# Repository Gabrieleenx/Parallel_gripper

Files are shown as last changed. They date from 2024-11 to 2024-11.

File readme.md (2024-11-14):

# Parallel gripper build guide

This is a build guide for the gripper used in the paper "Perception, Control and Hardware for In-Hand Slip-Aware Object Manipulation with Parallel Grippers", preprint available at: https://arxiv.org/abs/2410.19660. Everything is provided as is. 

The main repo for that project can be found at https://github.com/Gabrieleenx/Slip-Aware-Object-Manipulation-with-Parallel-Grippers 

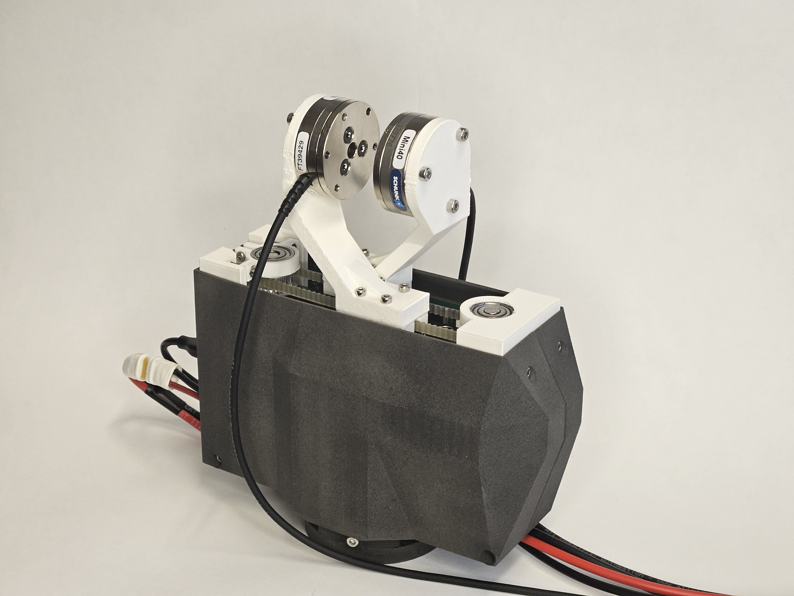
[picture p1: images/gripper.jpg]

## Overview 

This gripper was designed with the goal of having fast low-level force control and a high communication rate with a PC. We are controlling the gripper at 500 Hz, and it is possible to go faster. This readme is organized as follows:

* Overview of construction 
* Overview of code
* Part list
* Build guide

## Overview of construction
The construction of the gripper is fairly simple, it is after all only a parallel gripper. The main selling point is that we are using a bldc motor together with an encoder, which allows us to control it with FOC and get good motor characteristics, we are using SimpleFOC https://simplefoc.com/. The motor is then connected to a 2:1 gear reduction, which dives a pully with a belt on it. The fingers of the gripper run along 2 linear bearings. The motor is controlled by an ESP32 S3 microcontroller. We also deigned a quick connector for the UR10 mount.

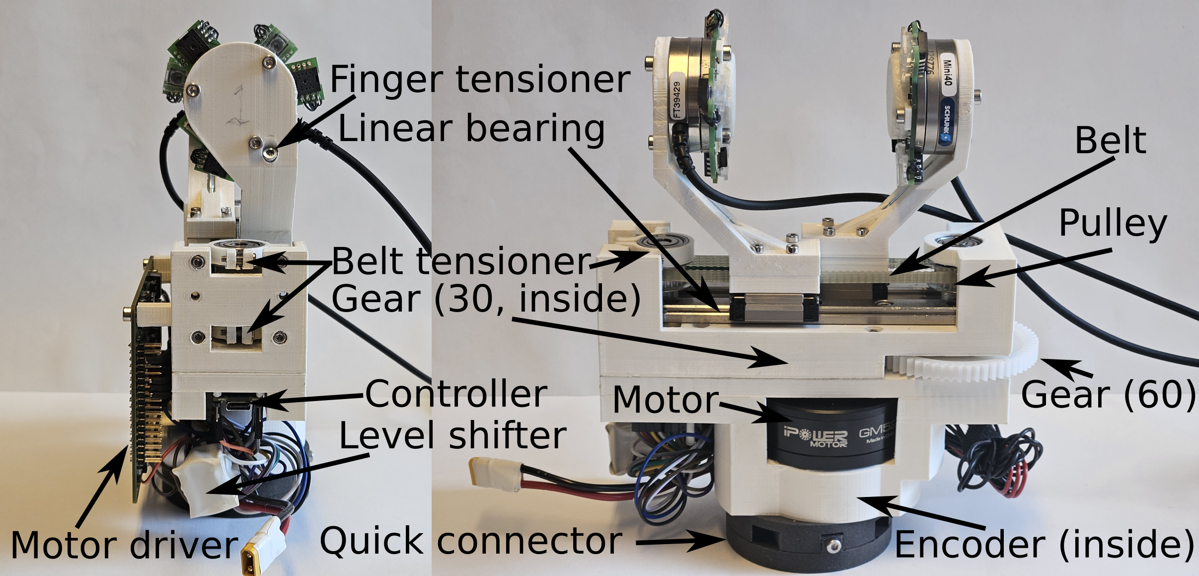
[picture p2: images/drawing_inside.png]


## Overview of code

All the code running on the ESP32 is in the gripper_code folder. The code to communicate with it from a pc can be found at https://github.com/Gabrieleenx/Slip-Aware-Object-Manipulation-with-Parallel-Grippers. The code differs slightly from the simpleFOC library, we implemented our own encoder class, this was to utilize the ESP32 built in pulse counter peripherals, instead of using interupts. And we have a bare minimum serial communication setup. Some of the reasoning to why, is that we had problems with the ESP32 S3 Nano from Arduino, where it would randomly stop commnicating. Unlike many other development boards it does not have a UART to USB chip and the USB communication is handeled internally on the ESP32. To get it to work properly we had to compile our code in debug mode to force it to use another part of the USB peripheral, (there probably is a better solution, but it worked and I had already spent way too much time debugging this).

We are using ardunio IDE 2.3.2 on Ubuntu 20, with simpleFOC library 2.3.4. Compiled with debug mode (Hardware CDC). 

The gripper outputs angle of the motor [RAD], and take commands on target voltage [-20.0 to 20.0], the sign determines the driection. 

## Part list 

### Compnents 

2x NSK Linear Guides LH100120ANK1B01PN1, LH, https://se.rs-online.com/web/p/linear-guides/4979411

1x Arduino nano esp32 (not with pre soldered pins) https://store.arduino.cc/en-se/products/nano-esp32?srsltid=AfmBOoq2j8PJsWTmrSQZ9lXL6lKOGxVrW5B-yabFGoDSFEEn9P-Iw4cd

1x iPower Motor GM5208-24 Brushless Gimbal Motor https://eu.robotshop.com/products/ipower-motor-gm5208-24-brushless-gimbal-motor

1x AMT103-D2048-I8000-S https://www.mouser.se/ProductDetail/Same-Sky/AMT103-D2048-I8000-S?qs=Jm2GQyTW%2FbhTj4QqD8fAHQ%3D%3D&mgh=1&gad_source=1&gclid=Cj0KCQiAoeGuBhCBARIsAGfKY7zdJklvF7jDlw4l8NdwcRQ16M22bnk4nwzr7osbEtRulv0hirsh0TkaAoGrEALw_wcB

1x DRV8302 Motor Drive Module https://www.aliexpress.com/i/4000126430773.html?gatewayAdapt=glo2fra (This is completly overkill and something like https://simplefoc.com/simplefoc_mini_product_v1 would be more appropiate, but was out of stock at the time, if you want current sensing, make sure the driver hardware supports it)

1x OPTIBELT 4 T2,5 / 265 Timing Belt, 106 Teeth, 265mm Length, 4mm Width https://se.rs-online.com/web/p/timing-belts/2171565 

2x OPTIBELT Timing Belt Pulley, Aluminium 4 mm, 6 mm Belt Width x 2.5mm Pitch, 22 Tooth https://se.rs-online.com/web/p/belt-pulleys/2362794 (these do not come pre-drilled!)

1x RS PRO POM 30 Teeth Spur Gear, 1 Module, 6mm Bore Diam, 30mm Pitch Diam, 14mm Hub Diam https://se.rs-online.com/web/p/spur-gears/5217540?searchId=529fef86-fb48-4f9c-933e-d6b7e4e49f6e&gb=s

1x RS PRO POM 60 Teeth Spur Gear, 1 Module, 8mm Bore Diam, 60mm Pitch Diam, 18mm Hub Diam https://se.rs-online.com/web/p/spur-gears/5217641?searchId=f93c0d57-8f67-4b74-b46d-4ea63853b34f&gb=s

1x Bosch Rexroth 0.4m Long Steel Closed Bush Shaft, 6mm Shaft Diam. , Hardness 60HRC, h6 Tolerance https://se.rs-online.com/web/p/linear-shafts/7243399 (This needs to be cut, and it is quite hard, alternativly is to buy an aluminium shaft which is much easier to work with)

I2C level shifter (atleast 2 channels) https://www.electrokit.com/nivaomvandlare-4-kanaler-bidirektionell-i2c?gad_source=1&gclid=Cj0KCQiA_qG5BhDTARIsAA0UHSI5S-Kx_KQxKBlJcykZjvEIinTe4hLcBaB7p3R2S9C23zfkMdlB-KEaAmAnEALw_wcB

### Wires and screws 
M1.6 [2x 6mm]

M2.5 [2x 6mm, 2x 8mm, 2x 10 mm, 8x 16 mm, 4x 20mm]

M3 [13x 8mm, 8x 10mm, 2x 14mm,4x 20mm, 3x 30mm, 1x 40mm, 2x 50mm]

M4 [3x 25 mm (or 20 mm should also work)]

You will need nuts (also 2x square nuts for m3, one for each finger), wires and dupont cables. 

### 3D printed parts
See stl_files folder for all the stl files. Almost all parts are printed in PLA and most with around 30% infil. Some of the parts has been slightly modified from the gripper in the pictures, this minimize the amount of post modification needed to the parts. 

Parts printed in PLA:
* belt_tensioner.stl
* bottom_part.stl
* drill_pully_holder.stl
* finger.stl (printed at 100 % infil)
* finger_base.stl (printed at 100 % infil)
* gear_spacer.stl  (printed at 100 % infil)
* middle_part.stl
* motor_to_gear.stl
* top_part.stl

The following parts where printed with an SLS printer (plastic), but they could be printed with normal FDM printing. 
* body_shell_1.stl
* body_shell_2.stl
* quick_adapter.stl
* UR_10_mount.stl 

The contact pads are printed with dual material
* contact_pad.stl outer part TPU95
* contact_pad.stl inner part PLA

### Other parts

* You will need a powersuply that can deliver 20 V and atleast 1A (preferably more, I use a bench power suply with adjustable volatage and current limits). 
* You will also need to get or create cables to connect the power supply with the motor driver, I have a small connector close to the gripper so that it is easy to diconnect. 
* I would recommed getting velcro strips for cable managment, I bolted some of them under the gipper to reduce forces on the contacts.
* You will need a USB cable, make sure it is a decent cable, otherwise power and communication issues might occure. 

## Build/Assembly guide

This an assembly guide for the gripper, an overview of the parts can be seen below:

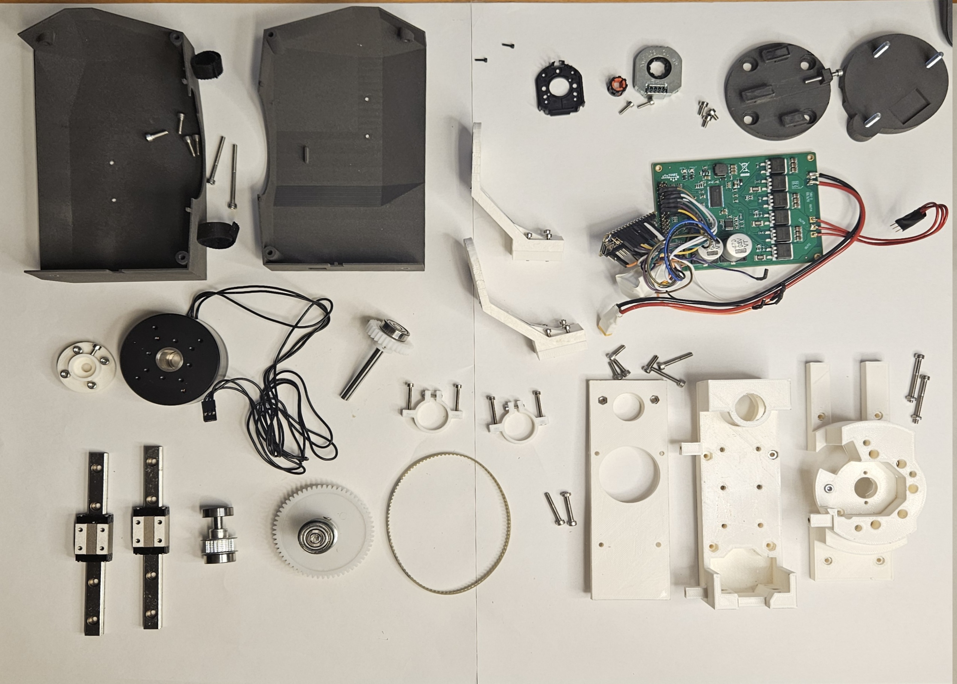
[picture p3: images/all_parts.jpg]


Start with cuting the 6mm shaft into 34mm, 60mm, and 48 mm lengths.  
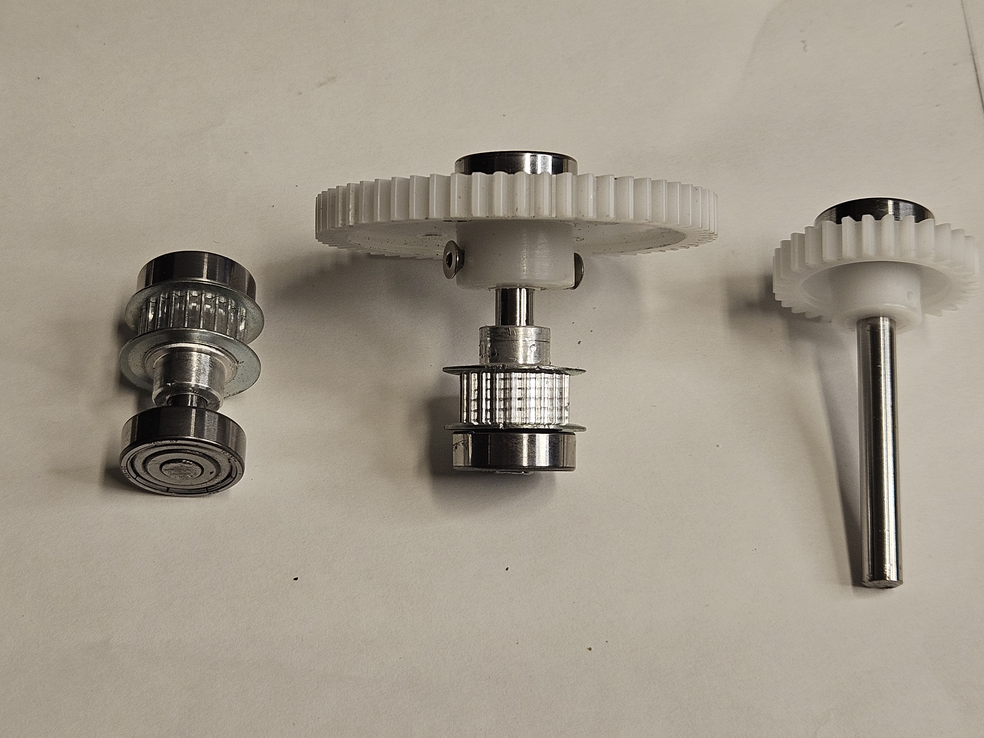
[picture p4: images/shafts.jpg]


Then drill 6mm holes in the pulley, they will be pressfitted on, so sligthly smaller than 6mm is preferable. You can use the 3D printed fixture to secure the pulley when drilling. It is important that the hole is in the center and straight, would recomend using a pillar drill.  

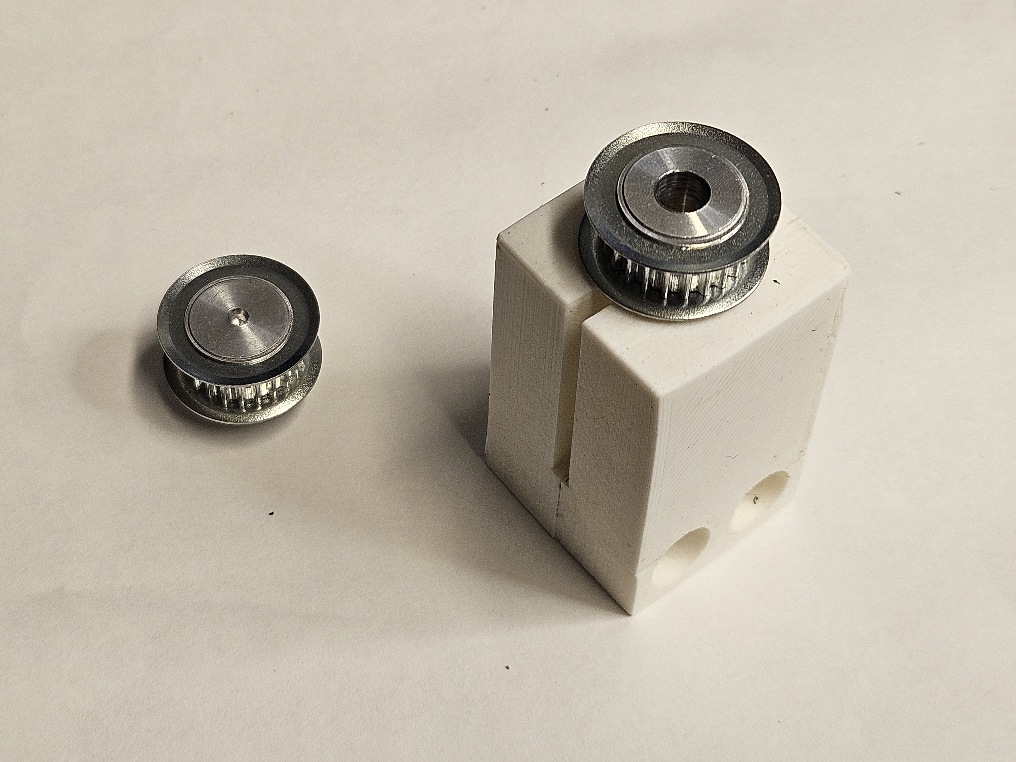
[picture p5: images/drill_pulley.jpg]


Put pulleys and bearings on, the gear big gear is put on with a spacer (3D printed) and two 2.5 mm diameter holes are drilled into the base of the gear, in each hole a M3, 6mm thread lenght countersunk screw are screwed in. The shaft is filed with flat spots for the scres to press against. The pulley is put on by pressfit and is tapped with a hammer at the base to secure it. 

2x m3 6mm thread countersunk screws. 

Insert M3 nuts,

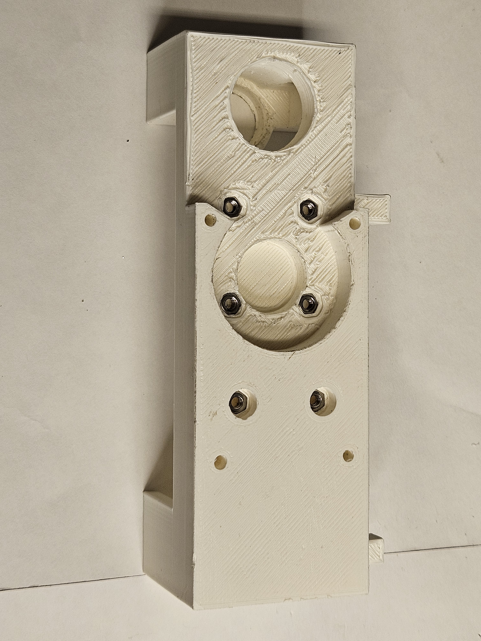
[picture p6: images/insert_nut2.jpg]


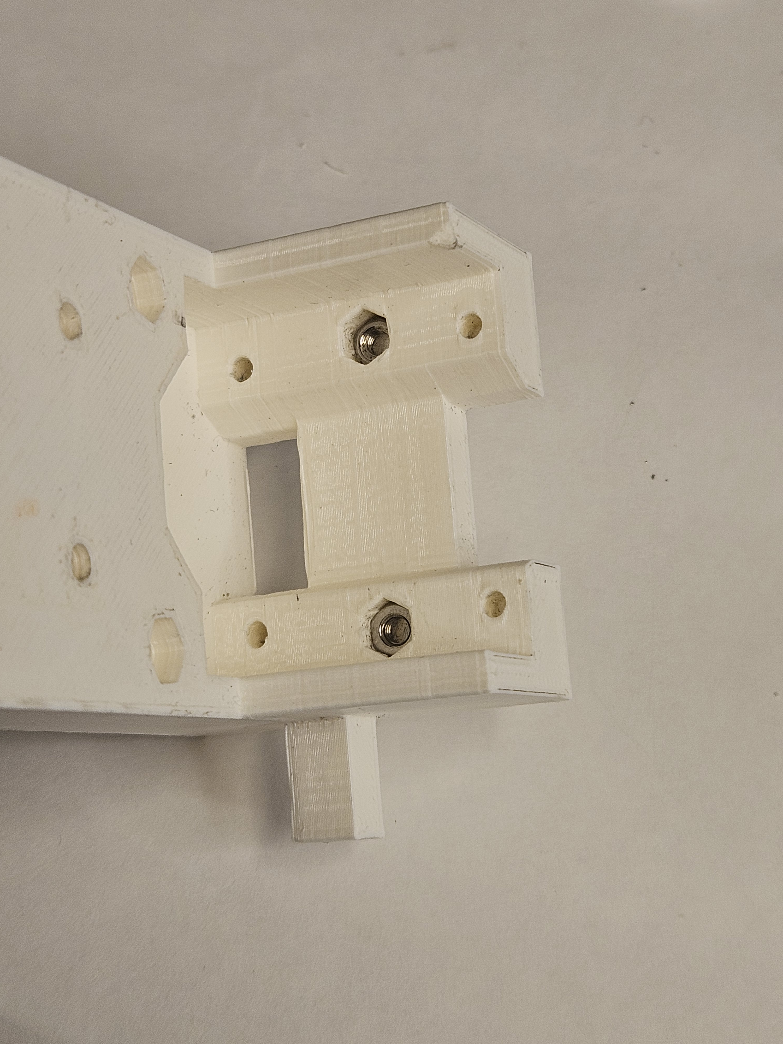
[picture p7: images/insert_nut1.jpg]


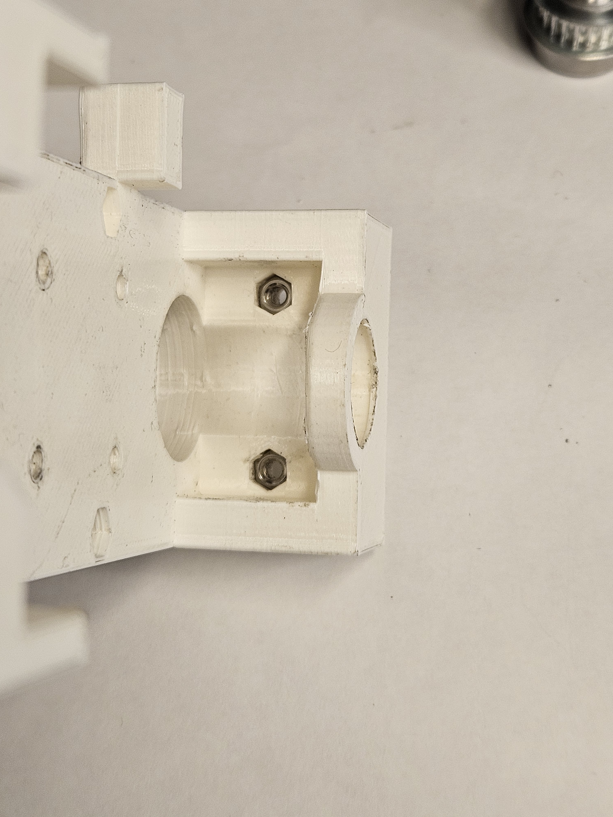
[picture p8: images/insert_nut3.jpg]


Insert the shaft with the big gear to the top part, and with the belt on.

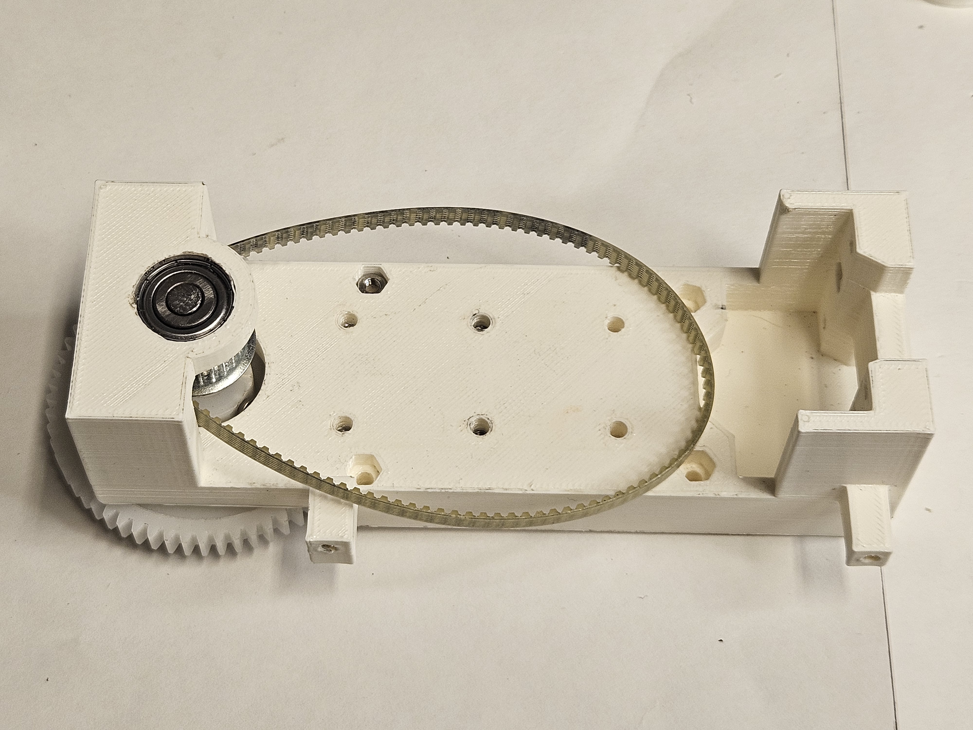
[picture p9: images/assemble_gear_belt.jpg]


Put the lower loop on the bearing 
1x m2.5 10 mm long, 

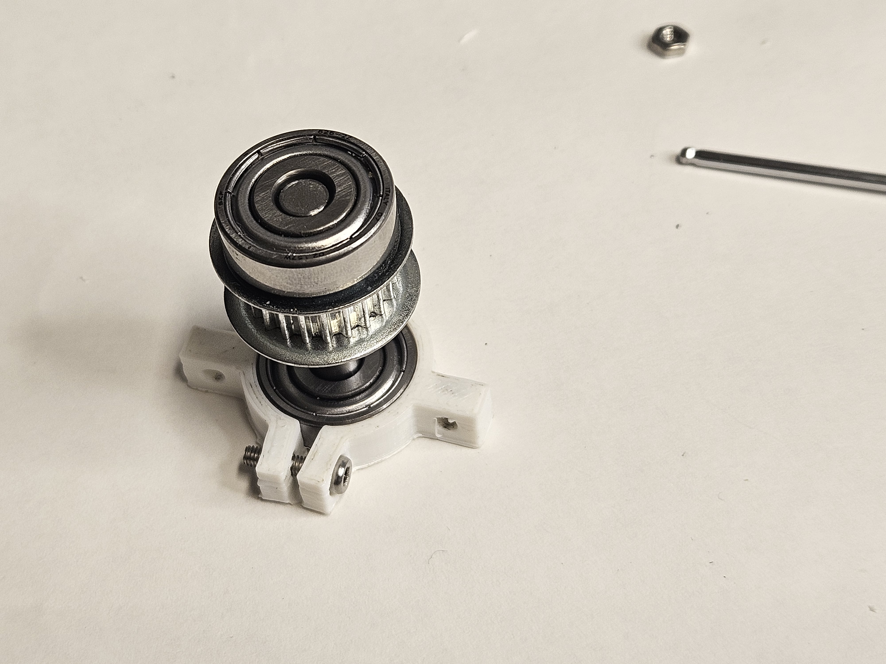
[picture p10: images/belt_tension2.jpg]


Assemble the part, but only losely, this can be a bit finiky. 
2x m2.5, 20mm screw

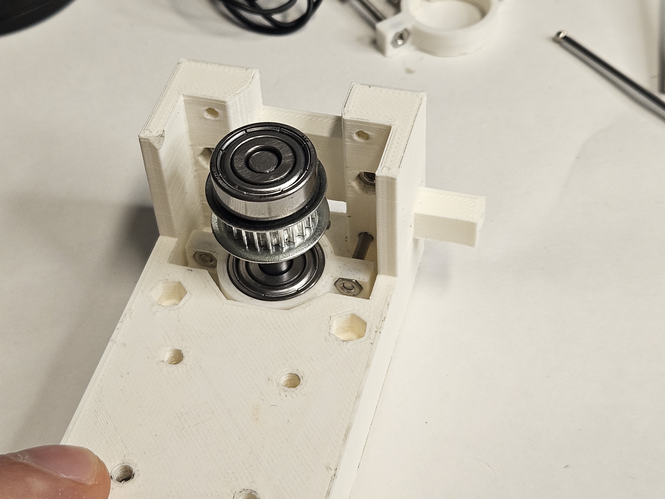
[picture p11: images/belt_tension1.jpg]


Wiggle in the two linear bearings, this it also a bit finiky. screw in with 2x m3 20mm and 4x m3 10mm, also be careful so that the slider doesn't fall of, some versions of linear bearings do not go easily together again (not sure about this one).   

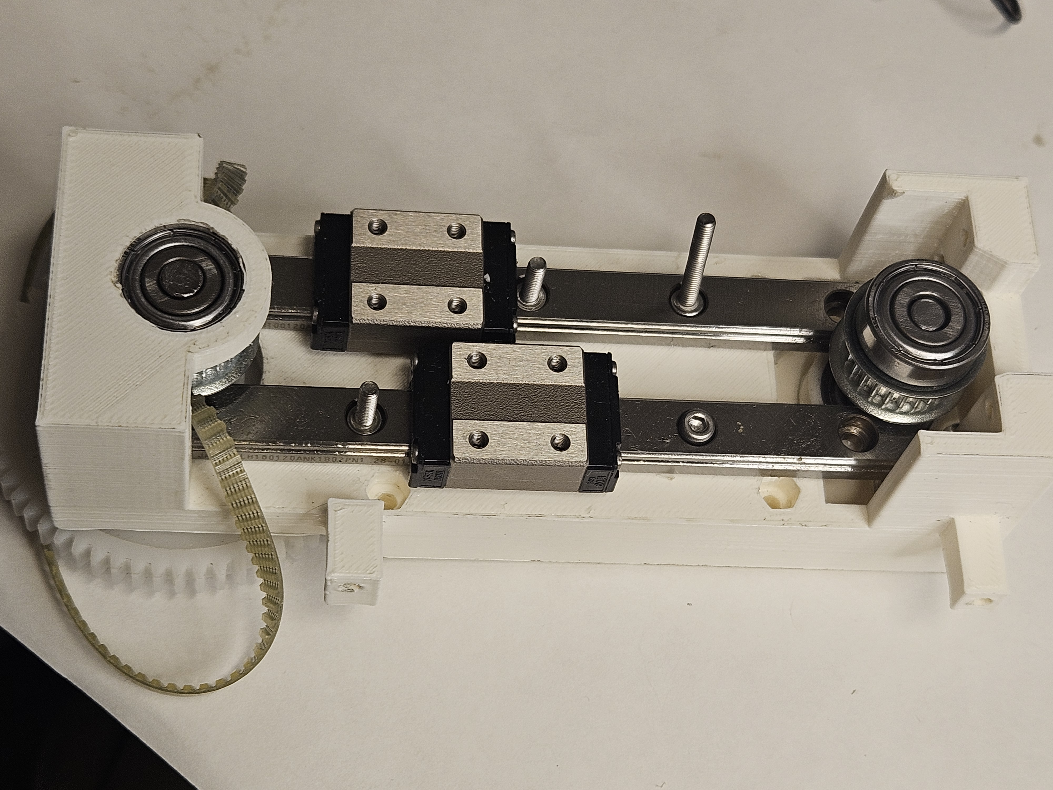
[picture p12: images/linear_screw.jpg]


Put the belt over the other pulley, and add the second loop 1x m2.5 10 mm, 2x m2.5, 20mm screw

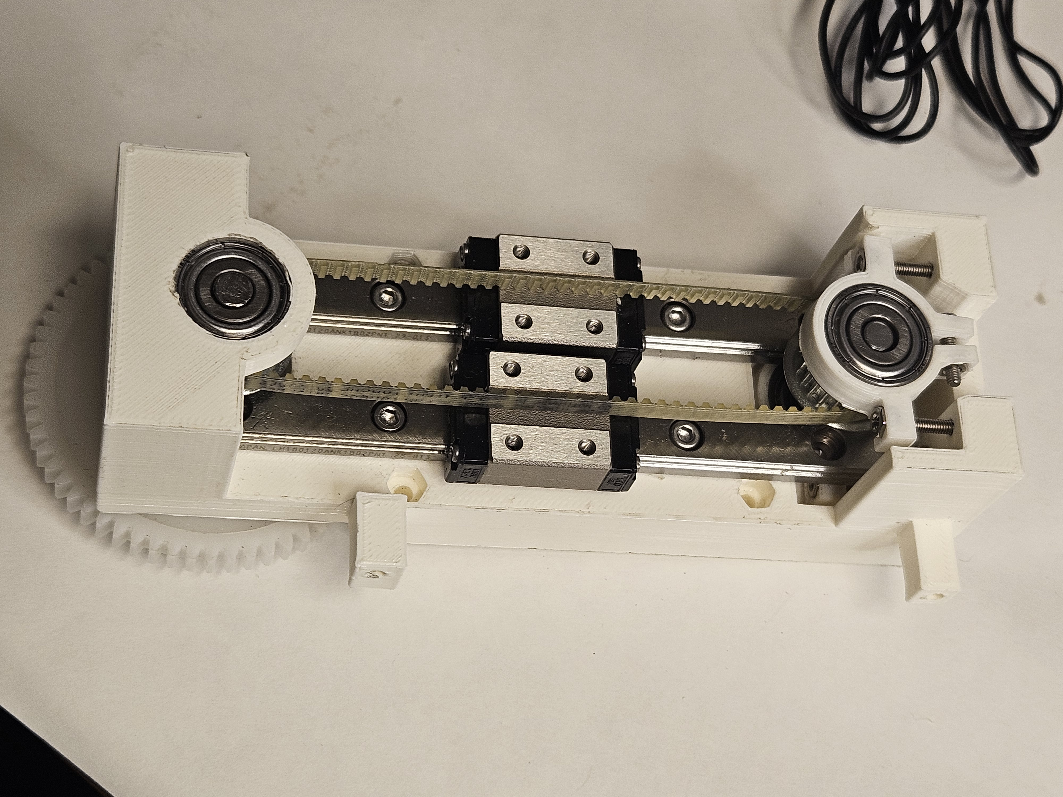
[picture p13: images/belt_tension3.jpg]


Install 2x m3 nuts, then install the middle plate with 2x m3 20 mm screws, make sure things can spin smoothly. 

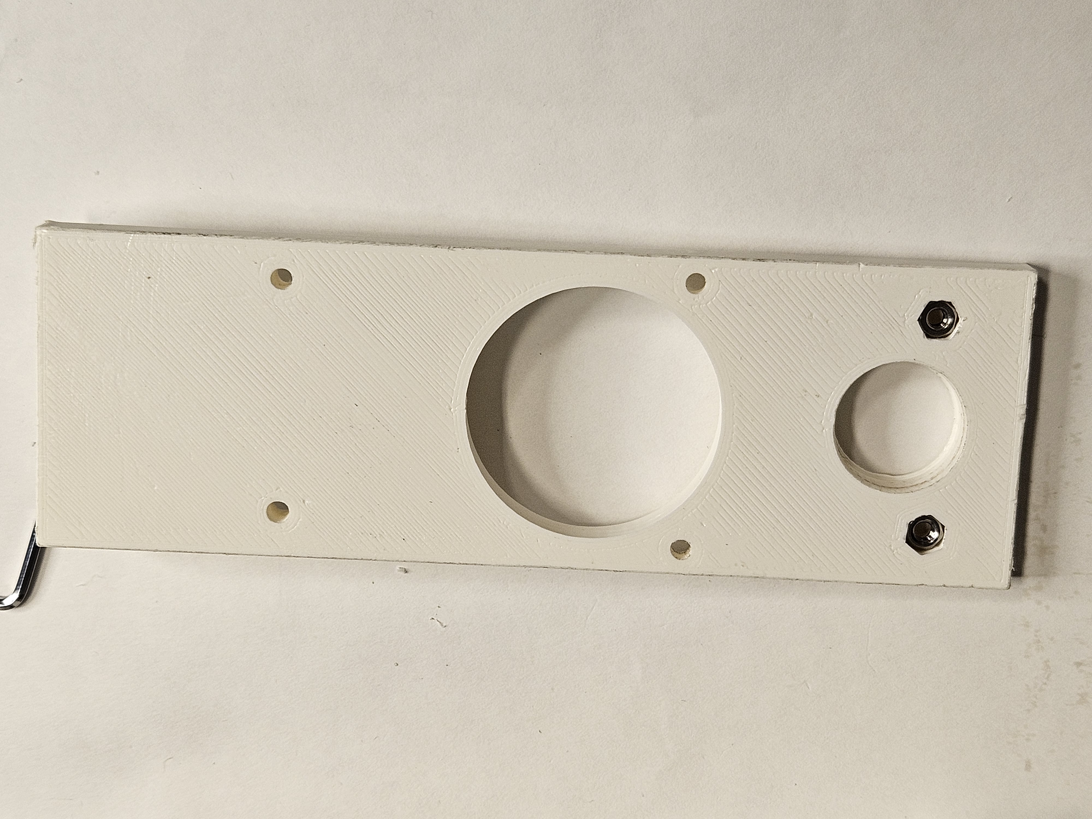
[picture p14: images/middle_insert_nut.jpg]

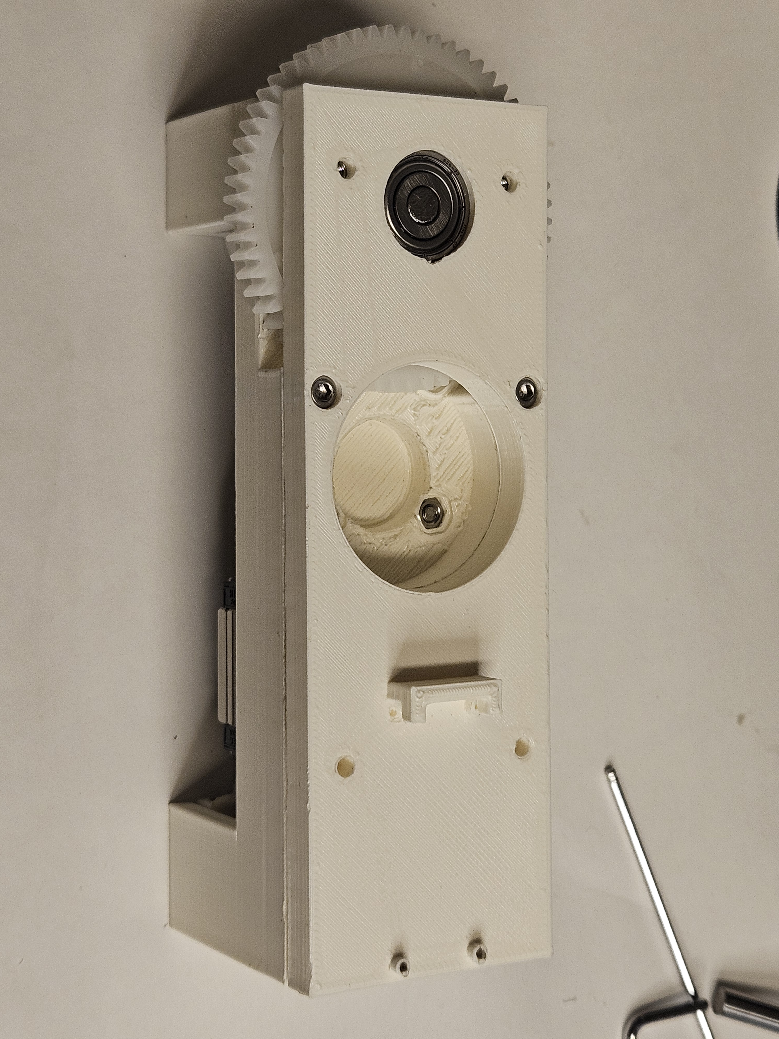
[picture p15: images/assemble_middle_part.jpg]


Put the assembly asside for now. 

Drill a hole in the small gear so that the motor got gear adapter can connect to it. 

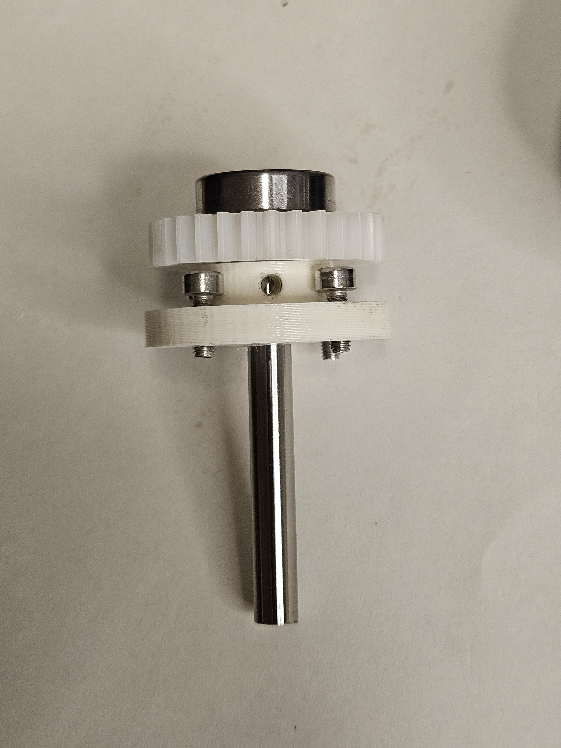
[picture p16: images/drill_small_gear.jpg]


Mount the adapter on the motor, 4x m3 8mm 

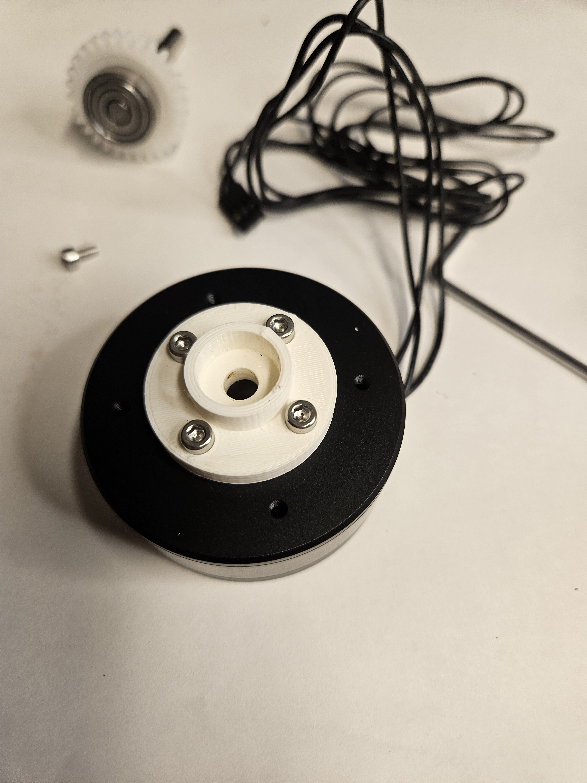
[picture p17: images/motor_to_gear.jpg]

Mount the gear to the motor with an M3 8mm screw. 
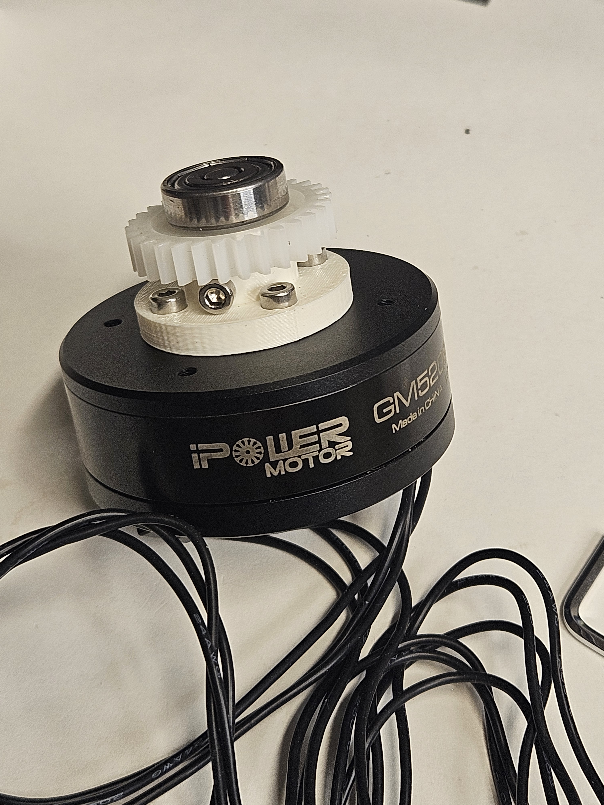
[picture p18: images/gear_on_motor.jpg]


Insert 2x m2,5 nuts and 3x m4 nuts in the botom part

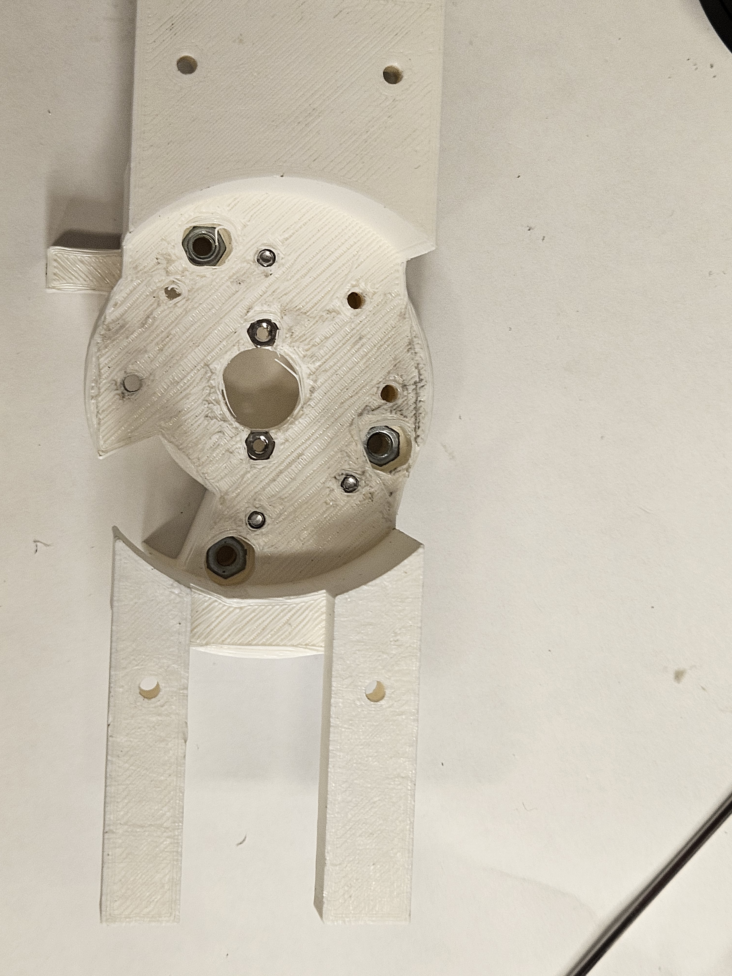
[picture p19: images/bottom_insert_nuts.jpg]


Mount the motor, I use 5x m3 8mm screws 

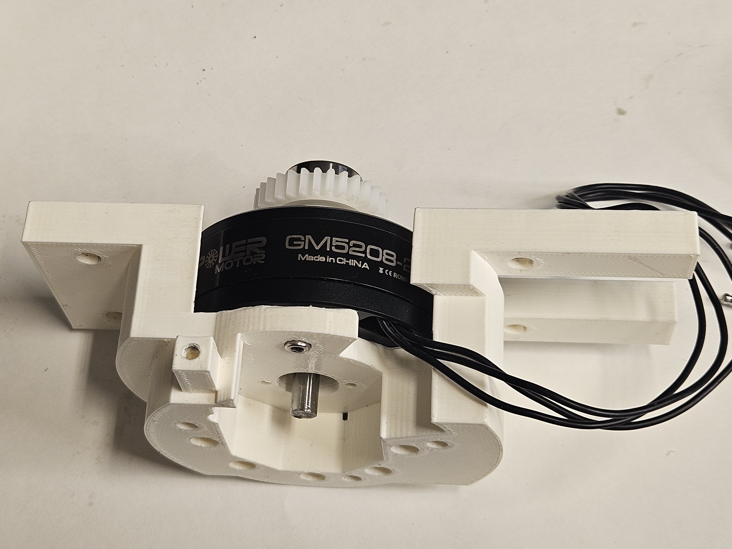
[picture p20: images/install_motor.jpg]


We can now mount the 2 assemblies together, with 2x m3 14mm and 2x m3 30 mm

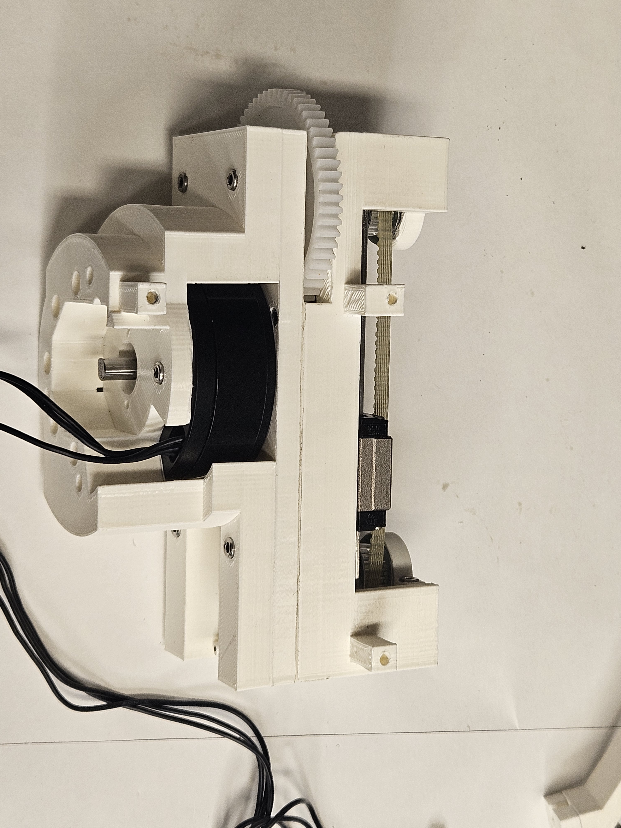
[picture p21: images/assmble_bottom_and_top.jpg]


Install the encoder with the tools provided and 2x m2.5 8mm screw. Make sure things still rotate freely. 

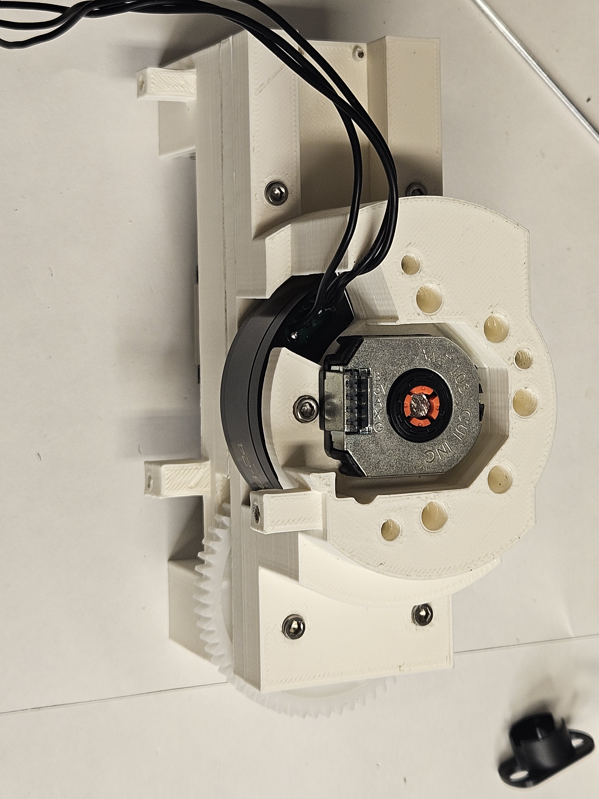
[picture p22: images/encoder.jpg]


Nextup, wire all the electronics, the schematics is found below. The dirver mounts with 3x m3 8mm and the aruino nano ESP32 with 2x m1.5 6mm. Take care so that the pins on the arduino is soldered on the side with the ESP 32, see figure below. You might need to flip the motor connector to get it rotating the correct direction. I bent the dupont connectors 90 deg and put heat shrink on it, the normal dupont connector is to large in some instances to mount, you could also solder the wires directly on. 
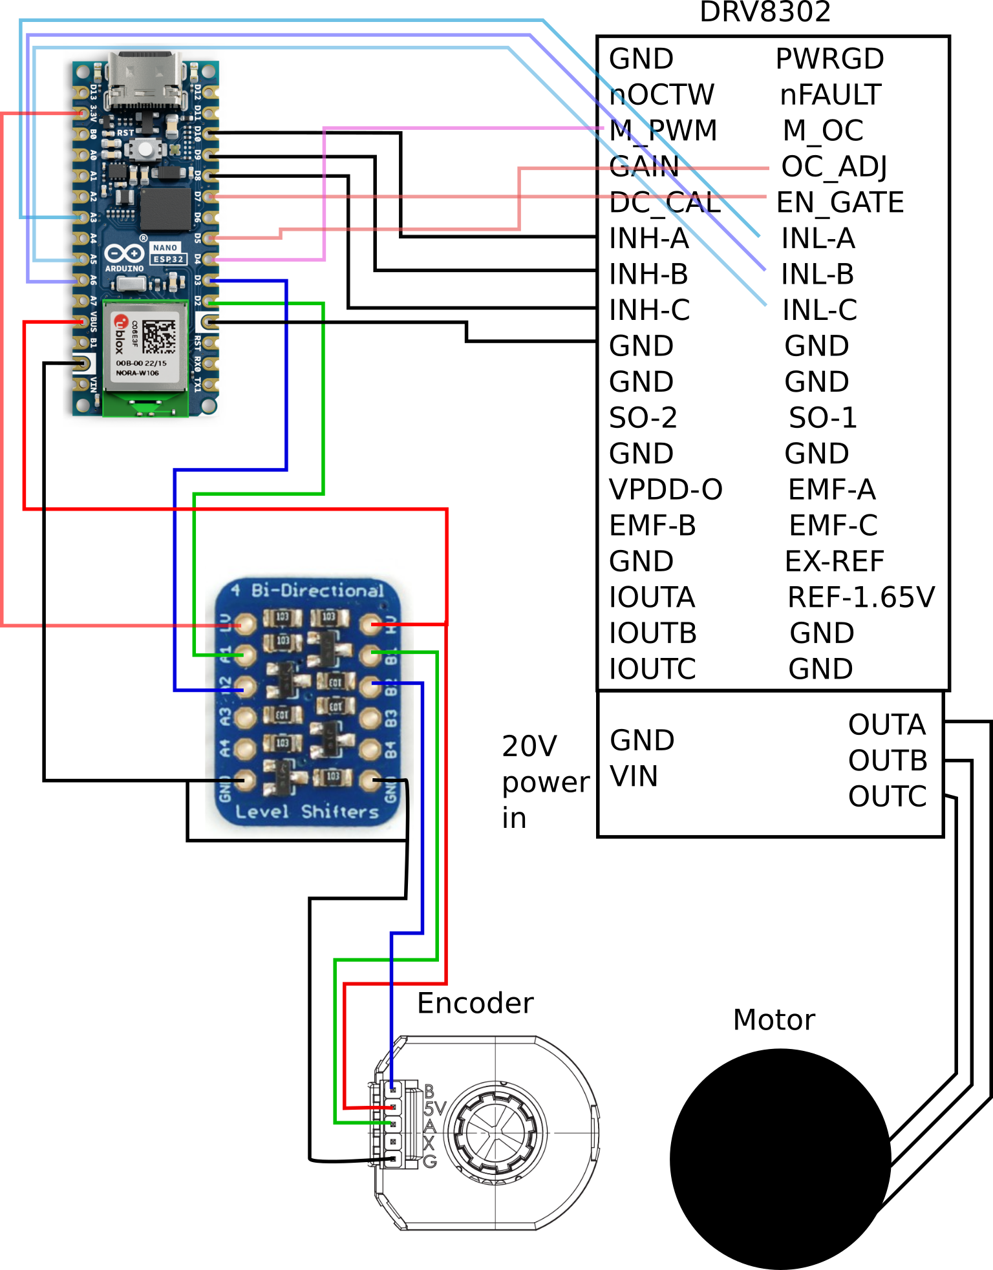
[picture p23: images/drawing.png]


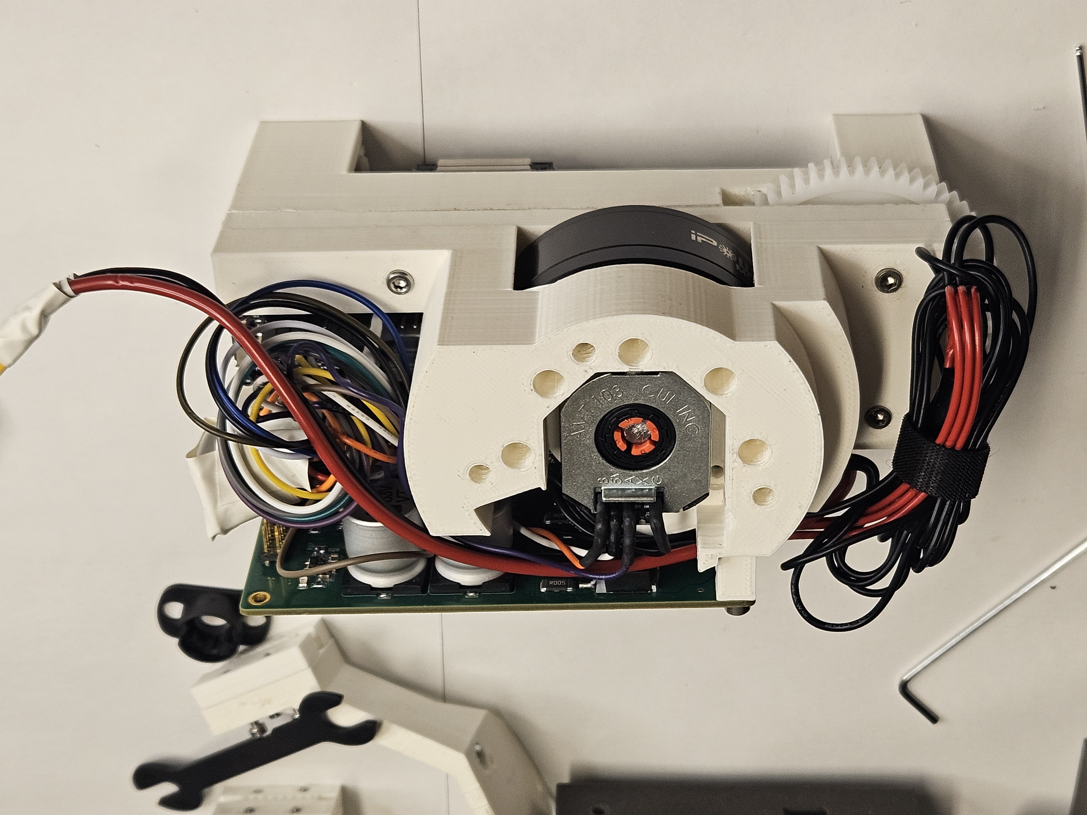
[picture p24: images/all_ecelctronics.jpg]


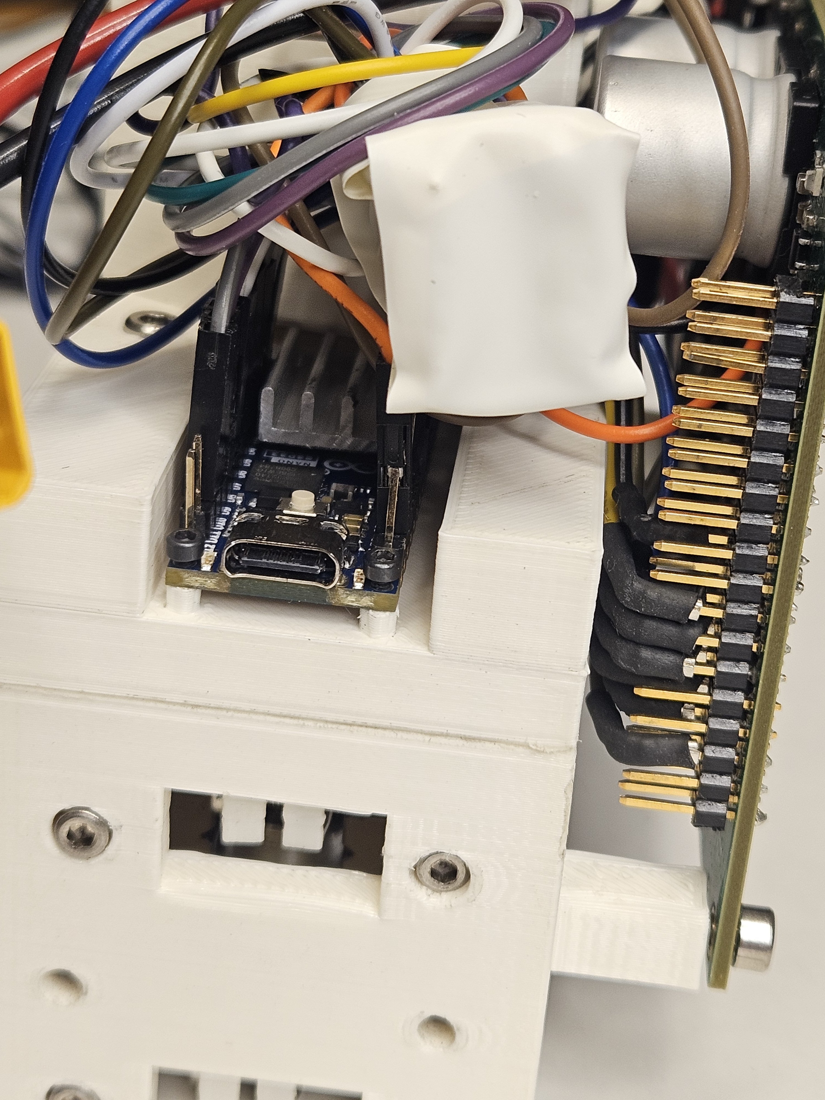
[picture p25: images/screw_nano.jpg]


I also put electrical tape around the voltage level shifter.

Mount the quick connector, 3x m4 25 mm, dont forget to place a m3 nut inside. The other part can den be attached with a single m3 20mm screw

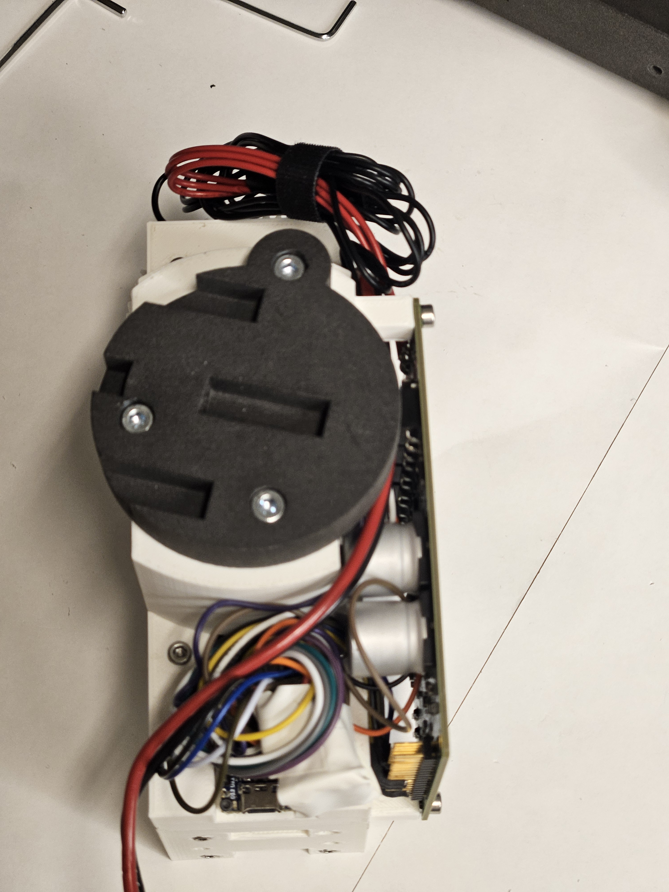
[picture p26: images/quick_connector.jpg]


Now tension the belt (make sure the belt tracks well on the pullys) and put on the finger base, 

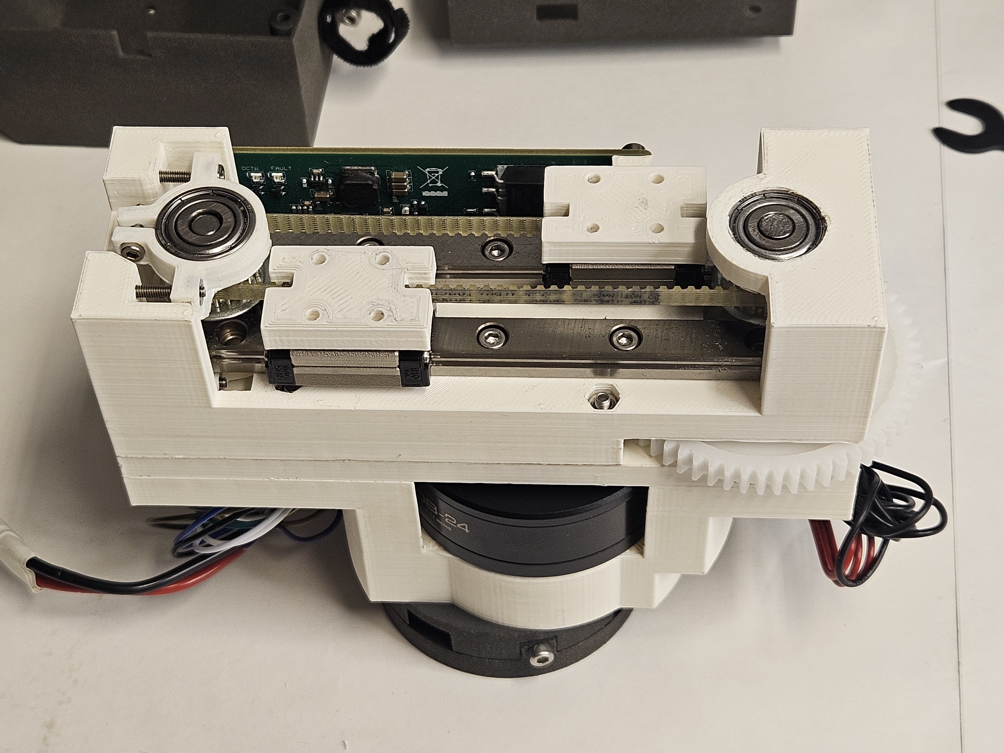
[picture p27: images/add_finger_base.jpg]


Each finger has a m3 50mm and square nut to increase stiffness. 

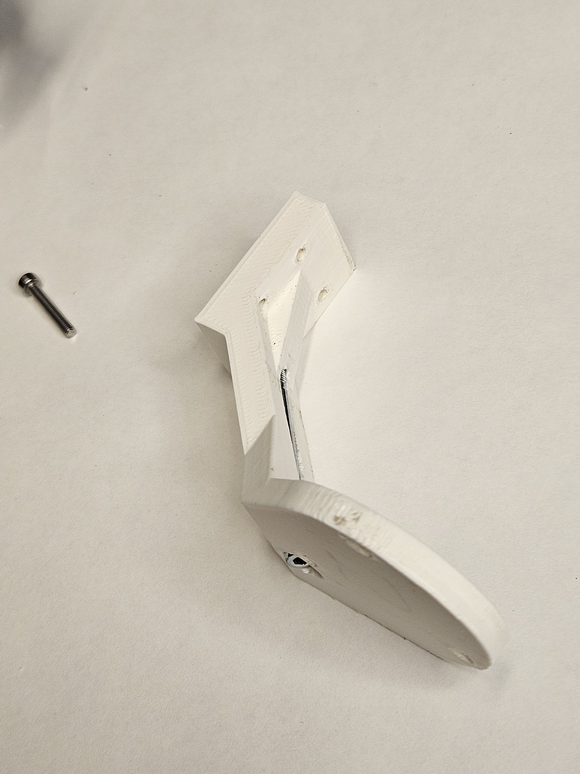
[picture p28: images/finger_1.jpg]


Mount each finger with 4x m2.5 16mm screws

Drill hole in shell to put velcro strips for cable managment, I secure the velcro with a m2,5 screw and nut. Put 2x m3 nuts in the shell, one is on the outside and one is on the insisde. Mount the shells with 4x m3 10mm, 1x m3 30 mm, and 1x m3 40mm 

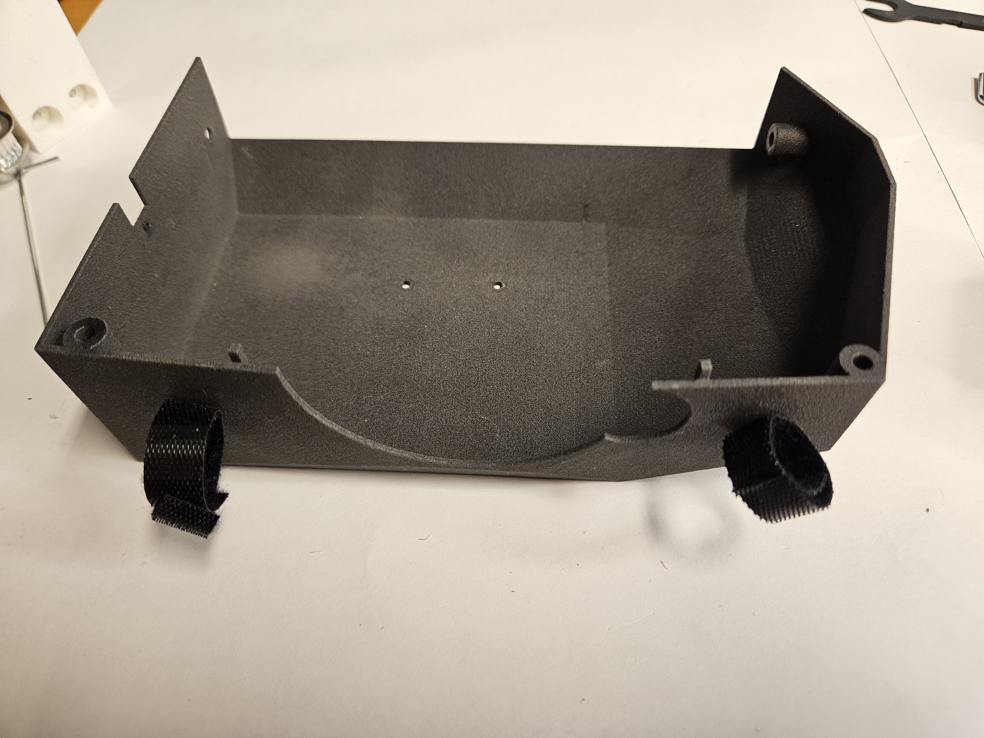
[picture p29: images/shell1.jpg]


Thhe gripper should now be finished, if you have problems with belt skipping, then you need to tension the belt more. Also make sure the belt tracks good when tensioning, the belt shouldn't try to move up or down.  

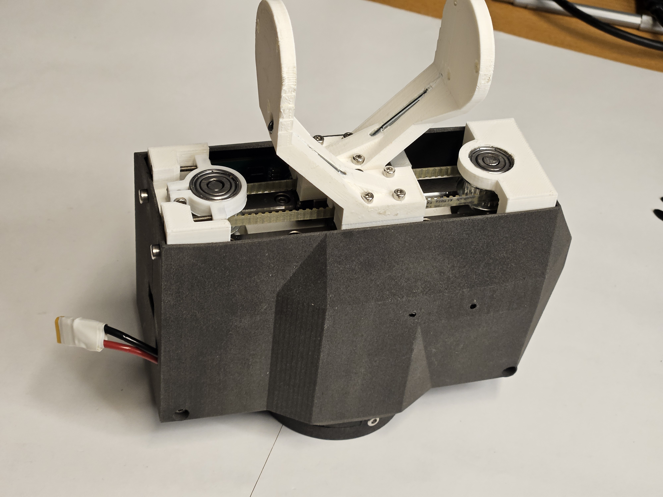
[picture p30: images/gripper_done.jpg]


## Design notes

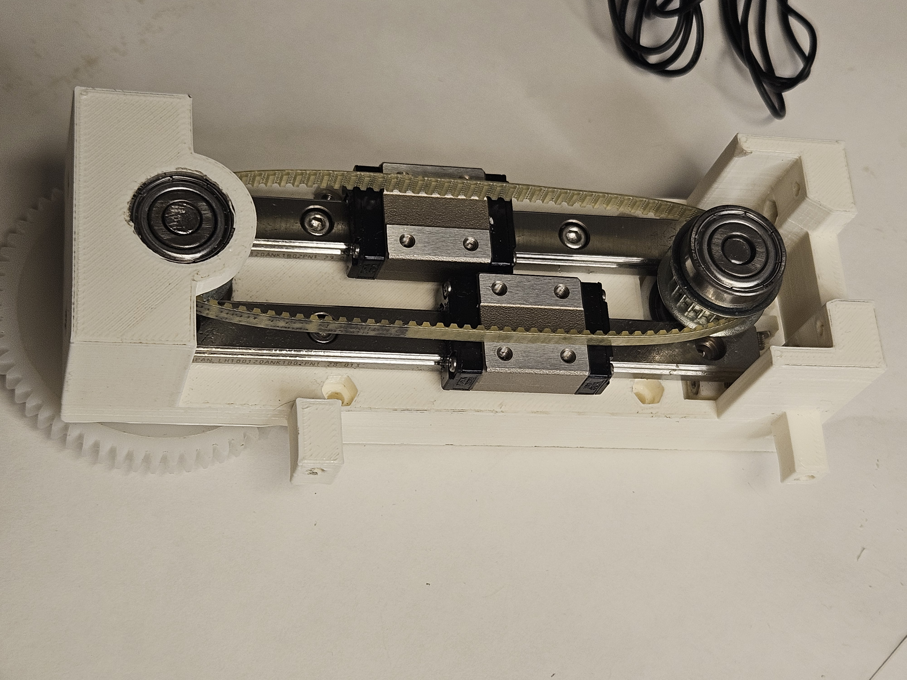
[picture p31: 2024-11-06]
images/belt1.jpg

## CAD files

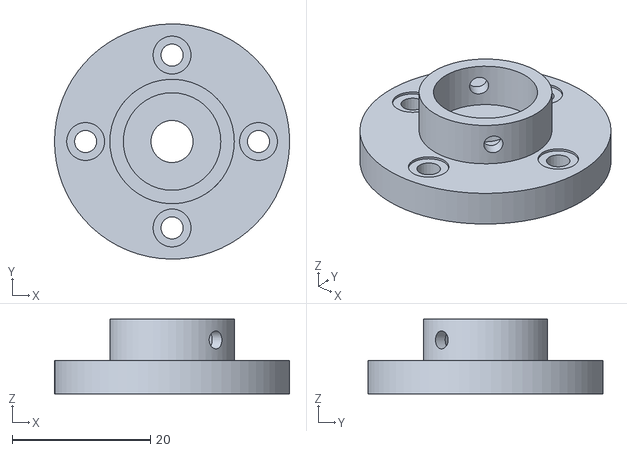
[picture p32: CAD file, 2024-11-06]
stl_files/motor_to_gear.stl
34.0 x 34.0 x 10.8

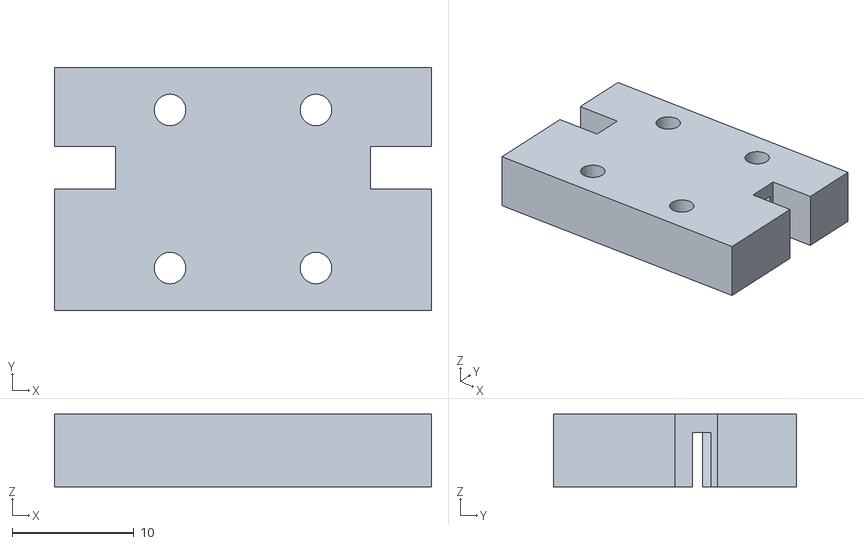
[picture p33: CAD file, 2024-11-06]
stl_files/finger_base.stl
31.0 x 20.0 x 6.00

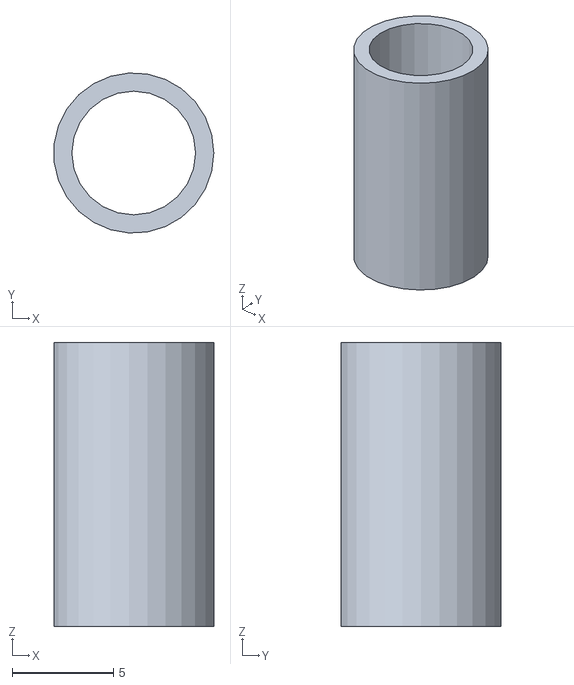
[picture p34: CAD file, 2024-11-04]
stl_files/gear_spacer.stl
7.87 x 7.89 x 14.0

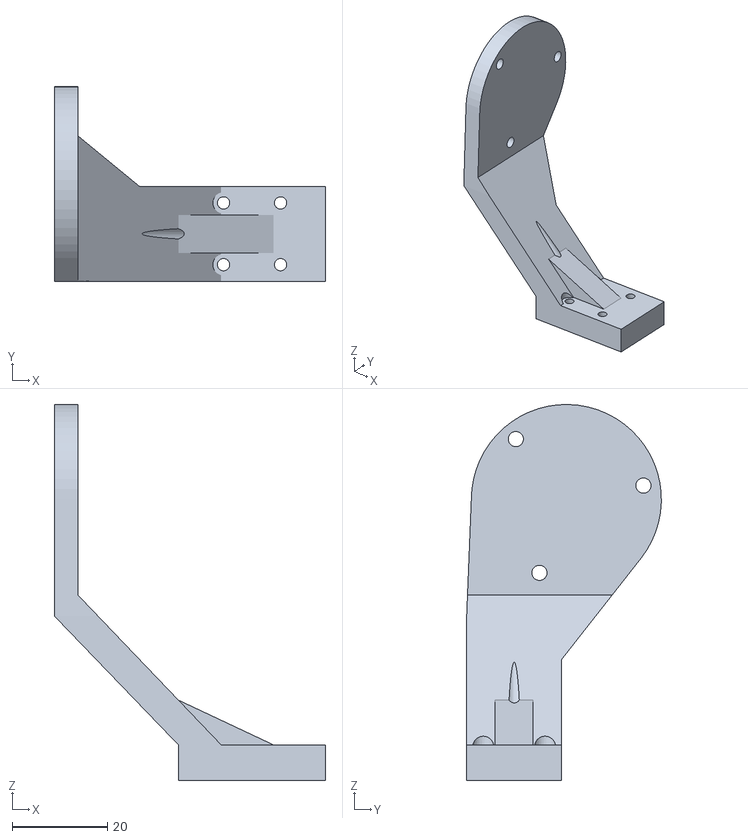
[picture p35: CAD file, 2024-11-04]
stl_files/finger.stl
57.1 x 41.0 x 79.1

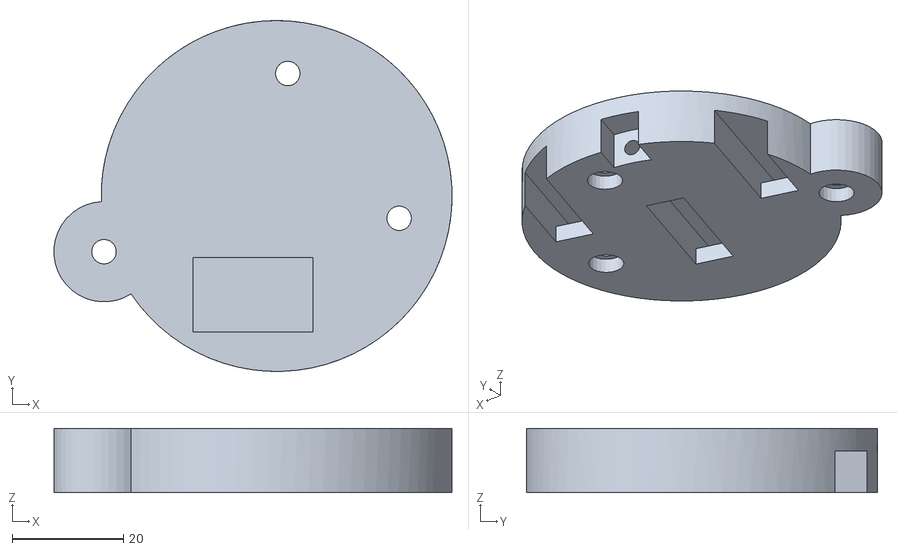
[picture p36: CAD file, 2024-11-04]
stl_files/quick_adapter.stl
71.5 x 63.0 x 11.5

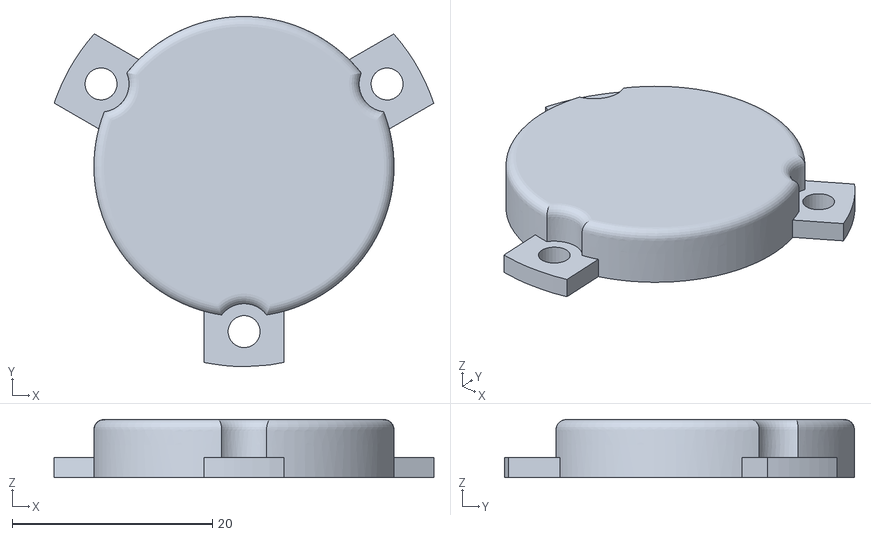
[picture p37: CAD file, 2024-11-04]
stl_files/contact_pad.stl
37.9 x 35.0 x 5.80

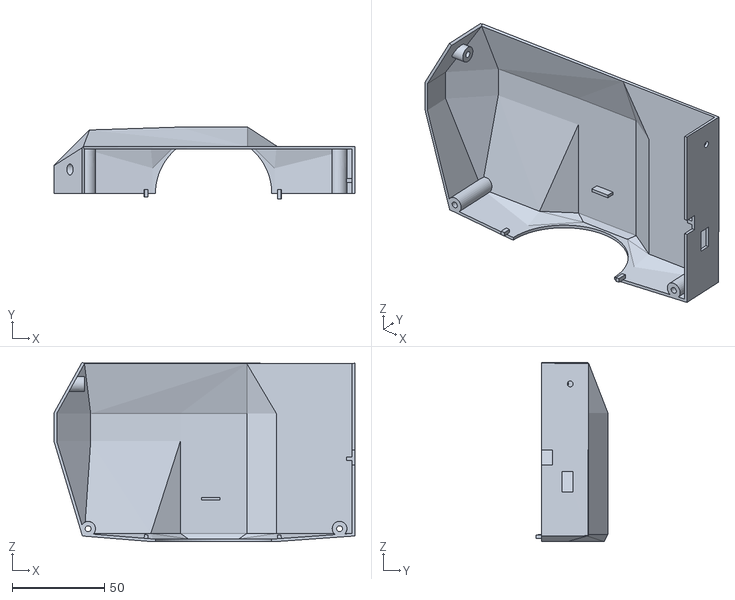
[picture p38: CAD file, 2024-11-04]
stl_files/body_shell_1.stl
163.1 x 39.0 x 97.2

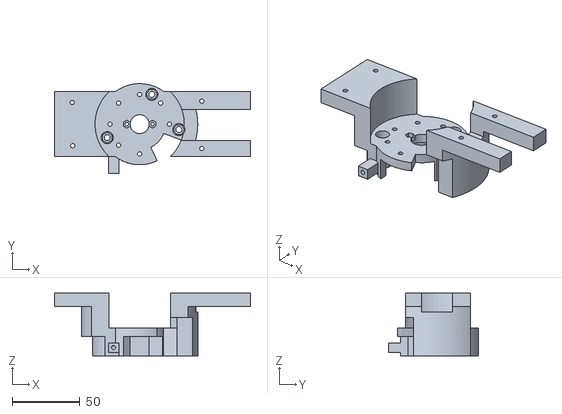
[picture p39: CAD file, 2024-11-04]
stl_files/bottom_part.stl
145.0 x 66.4 x 46.5

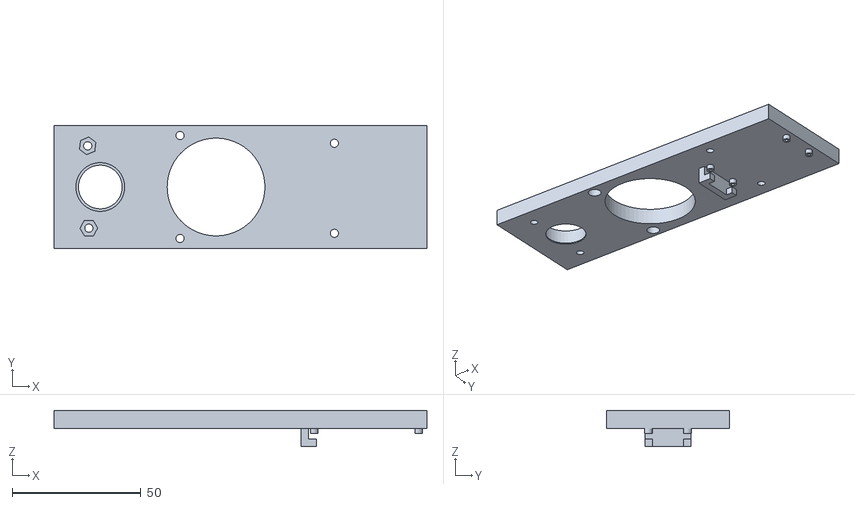
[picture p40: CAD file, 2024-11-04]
stl_files/middle_part.stl
145.0 x 48.0 x 14.0

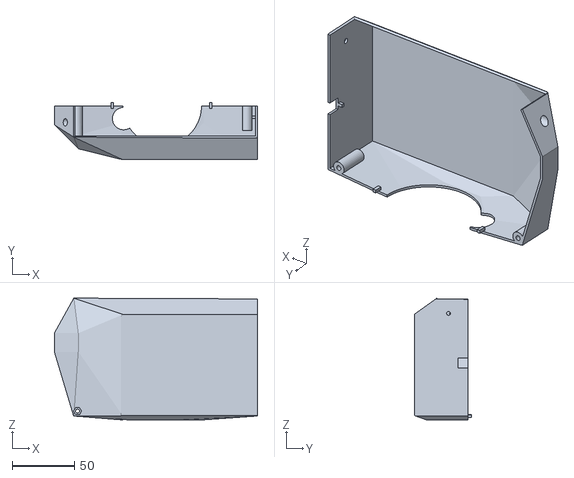
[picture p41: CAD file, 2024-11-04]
stl_files/body_shell_2.stl
163.0 x 45.9 x 97.7

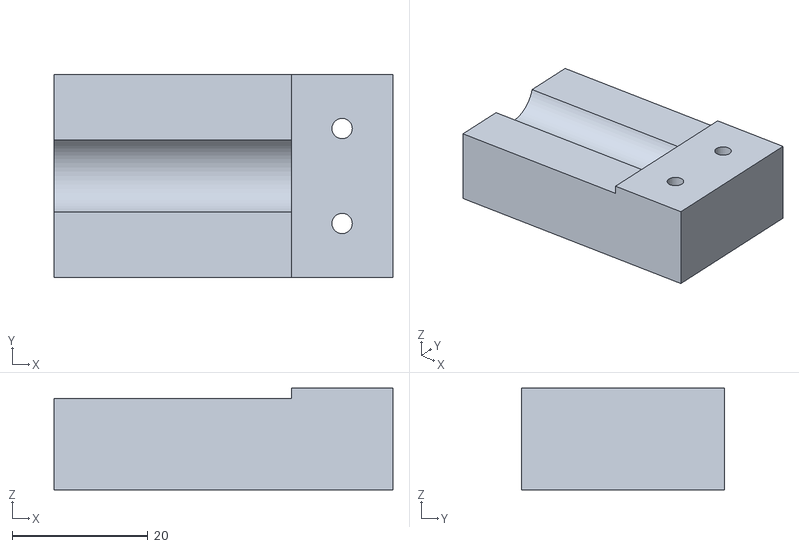
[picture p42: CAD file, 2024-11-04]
stl_files/drill_pully_holder.stl
50.0 x 30.0 x 15.0

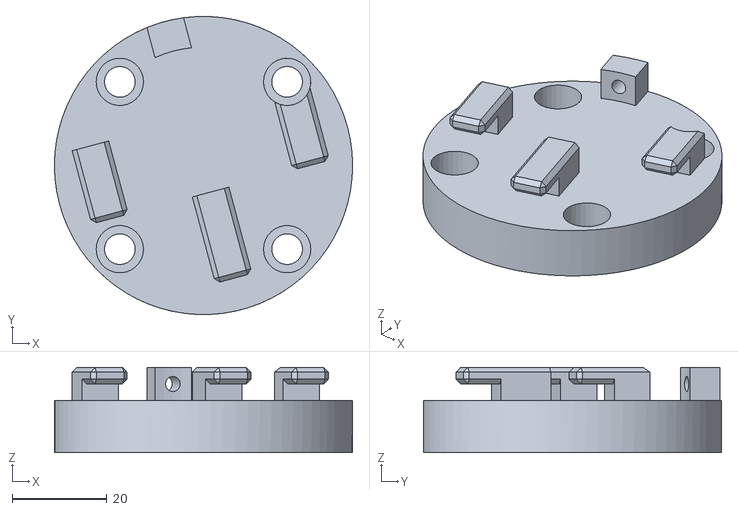
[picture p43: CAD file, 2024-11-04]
stl_files/UR_10_mount.stl
63.0 x 63.0 x 18.0

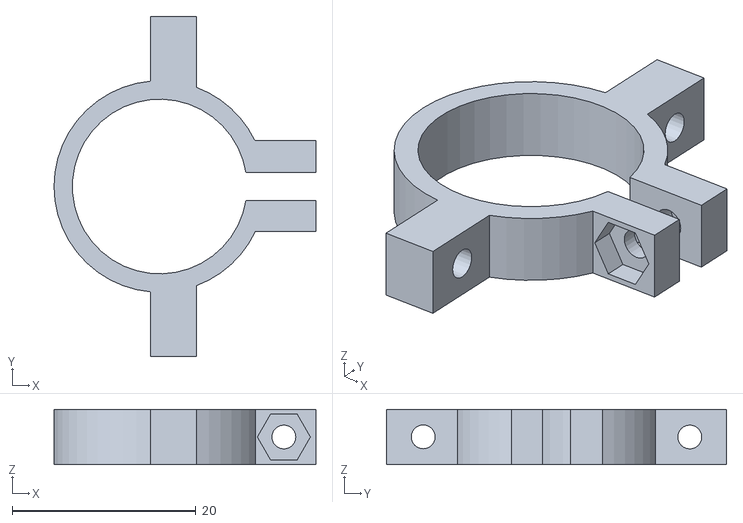
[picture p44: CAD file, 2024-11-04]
stl_files/belt_tensioner.stl
28.5 x 37.0 x 6.00

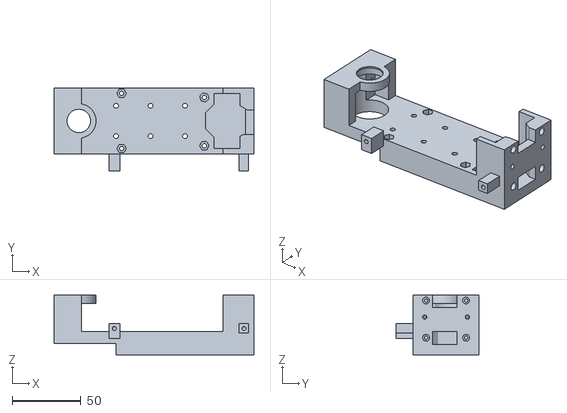
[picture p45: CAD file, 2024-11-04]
stl_files/top_part.stl
145.0 x 60.4 x 43.5

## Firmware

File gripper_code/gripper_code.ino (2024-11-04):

/**
 * Comprehensive BLDC motor control example using encoder and the DRV8302 board
 *
 * Using serial terminal user can send motor commands and configure the motor and FOC in real-time:
 * - configure PID controller constants
 * - change motion control loops
 * - monitor motor variabels
 * - set target values
 * - check all the configuration values
 *
 * check the https://docs.simplefoc.com for full list of motor commands
 *
 */

/* 
Not using serial commander due to problems when using it together with an encoder with interupts.
The serial communication happens on core 0 and all rest including interups happens on core 1*/
#include <SimpleFOC.h>
#include <encoder_pcnt.h>

//#include "driver/temp_sensor.h"

// DRV8302 pins connections
// don't forget to connect the common ground pin
#define INH_A 21 //gpio D10
#define INH_B 18 //gpio D9
#define INH_C 17 //gpio D8
#define INL_A 4  //gpio A3
#define INL_B 13 //gpio A6
#define INL_C 12 //gpio A5


// Normal Pin numbering 
#define EN_GATE 7 // D7 gpio 10
#define M_PWM 4 // D4 gpio 7
#define OC_ADJ 5 // D5 gpio 8

unsigned int  monitor_decimals = 4; //!< monitor outputs decimal places
int hz = 500;
// FreeRTOS handles for the tasks
TaskHandle_t mainTaskHandle;
TaskHandle_t serialTaskHandle;
SemaphoreHandle_t mutex;

// Define the data structure to be sent via the queue
struct Data {
  float value;
};


// Motor instance
BLDCMotor motor = BLDCMotor(11);
//BLDCDriver3PWM driver = BLDCDriver3PWM(INH_A, INH_B, INH_C, EN_GATE);
BLDCDriver6PWM driver = BLDCDriver6PWM(INH_A,INL_A, INH_B,INL_B, INH_C,INL_C, EN_GATE);

// DRV8302 board has 0.005Ohm shunt resistors and the gain of 12.22 V/V

// encoder instance
//EncoderPCNT encoder = EncoderPCNT(5, 6, 2048); // GPIO D2, D3
EncoderPCNT encoder = EncoderPCNT(5, 6, 4096); // GPIO D2, D3


bool readSerial(char* msg, int& msg_cnt){
  try{
    while (Serial.available()) 
    {
      // get the new byte:
      char ch = Serial.read();
      // end of user input
      if (ch == '\n') {
        return 1;
      }
      msg[msg_cnt] = ch;
      msg_cnt += 1;
      if (msg_cnt >20){
        Serial.println("Too long in read");
        msg_cnt = 0;
      }
    }
  }
  catch (...){
    Serial.println("Something wrong in read");
  }


  return 0;
}



void setup() {
  
  // initialize encoder sensor hardware
  encoder.init();
  // link the motor to the sensor
  motor.linkSensor(&encoder);
  // DRV8302 specific code
  // M_OC  - enable overcurrent protection
  pinMode(M_PWM,OUTPUT);
  digitalWrite(M_PWM, LOW);
  pinMode(OC_ADJ,OUTPUT);
  digitalWrite(OC_ADJ, HIGH);
  setCpuFrequencyMhz(240);
  
  // driver config
  // power supply voltage [V]
  driver.voltage_power_supply = 20;
  //driver.dead_zone = 0.05;

  //driver.pwm_frequency = 5000;
  driver.init();
  
  // link the motor and the driver
  motor.linkDriver(&driver);
  // link current sense and the driver
  // align voltage
  motor.voltage_sensor_align = 6;
    // choose FOC modulation
  motor.foc_modulation = FOCModulationType::SpaceVectorPWM;
  //motor.foc_modulation = FOCModulationType::SinePWM;
  // control loop type and torque mode 
  motor.torque_controller = TorqueControlType::voltage;
  motor.controller = MotionControlType::torque;
  //motor.motion_downsample = 1.0;
  
  // velocity loop PID
  motor.PID_velocity.P = 0.2;
  motor.PID_velocity.I = 5.0;
  // Low pass filtering time constant 
  motor.LPF_velocity.Tf = 0.02;
  // angle loop PID
  motor.P_angle.P = 20.0;
  // Low pass filtering time constant 
  motor.LPF_angle.Tf = 0.0;
  // current q loop PID 
  motor.PID_current_q.P = 3.0;
  motor.PID_current_q.I = 100.0;
  // Low pass filtering time constant 
  motor.LPF_current_q.Tf = 0.02;
  // current d loop PID
  motor.PID_current_d.P = 3.0;
  motor.PID_current_d.I = 100.0;
  // Low pass filtering time constant 
  motor.LPF_current_d.Tf = 0.02;

  // Limits 
  motor.velocity_limit = 100.0; // 100 rad/s velocity limit
  motor.voltage_limit = 20.0;   // 12 Volt limit 
  motor.current_limit = 1;    // 2 Amp current limit

  
  _delay(500);
  // use monitoring with serial for motor init
  // monitoring port
  
  Serial.begin(115200);// Create a HardwareSerial object
  //Serial1.begin(115200, SERIAL_8N1, D12, D13);
  
  //Serial.setDebugOutput(true);
  //Serial.setTxTimeoutMs(0); 
  //Serial.enableReboot(false);
  
  //Serial.setRxBufferSize(1024);

  while (Serial != true){
    delay(10);
  }


  // comment out if not needed
  //motor.useMonitoring(Serial);
  //motor.monitor_variables = _MON_TARGET | _MON_VEL | _MON_ANGLE; // monitor the two currents d and q
  //motor.monitor_variables = _MON_ANGLE; // monitor the two currents d and q
  //motor.monitor_downsample = 1;
  //motor.monitor_decimals = 3;
  //motor.modulation_centered	= false; Lowers standby voltage but not, the resistance of movment at 0 voltage
  // initialise motor
  motor.init();

  // align encoder and start FOC

  motor.initFOC();
  // set the inital target value
  motor.target = 0.0;

  Serial.println(F("Voltage control"));
  _delay(1000);
}


const int max_input_lenght = 20;
char received_chars[max_input_lenght+3] = {0}; //!< so far received user message - waiting for newline
int rec_cnt = 0; //!< number of characters receives
Data data;
//String msg = "";
int msg_length = 0;
unsigned long previousMicros = micros();    // Stores the last time loop ran
unsigned long currentMicros = micros();    // Stores the last time loop ran
const long interval = int(1e6/hz);          // Interval in milliseconds

void loop() {

  motor.loopFOC();
  motor.move(); 

  currentMicros = micros();
  if (currentMicros - previousMicros >= interval){
    previousMicros = currentMicros;
    float angle = motor.shaft_angle;
    Serial.println(angle, monitor_decimals);
  }


  if (readSerial(received_chars, rec_cnt)){
    if (received_chars[0] == 'T'){
      // Create a buffer to hold the substring
      char substring[rec_cnt] = {0}; // +1 for the null terminator
      //memset(substring, 0, rec_cnt); // Ensure it's null-terminated
      // Copy the characters from received_chars to substring
      for (int i = 0; i < rec_cnt-1; i++) {
        substring[i] = received_chars[1 + i];
      }
      try{
      float result = atof(substring); 
      motor.target = result;
      }catch(...){
        Serial.println("Converstion failed");
      }
    } 
    rec_cnt = 0;
  }
  if (rec_cnt >= max_input_lenght){
    Serial.println("Too long"); 
    rec_cnt = 0;
  }

}
